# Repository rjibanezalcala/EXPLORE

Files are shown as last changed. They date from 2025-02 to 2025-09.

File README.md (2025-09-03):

---

---

<h1 id="welcome-to-explore">Welcome to EXPLORE!</h1>
<p>EXPLORE stands for microElectrode eXperimental kit with Probe LOcation Rationalization in Electrophysiology. EXPLORE is an open-source collection of 3D-printed devices and protocols which aim to provide neuroscientists tools, methods, and guidelines to carry out electrophysiological experiments in rodents.</p>
<p>Here we provide 3D-printable files for our custom-made, modular, adjustable chronic implant designed to house one or two microelectrode array probes (such as the <a href="https://www.neuropixels.org">Neuropixels probes</a> or <a href="https://plexon.com/products/neural-electrodes-probes-and-arrays/">Plexon probes</a>). You will also find our custom “implant accessories”, including our implant stereotaxic holder, assembly kit, and testing kit. Last, but not least, we have designed KEPLER, a precision screwdriver which aims to assist in making micrometer-adjustments to the vertical position of the probe(s) as they are slowly introduced into the brain tissue within the implant.</p>
<p>Everything in this repository can be printed completely in-house with a consumer-grade SLA 3D printer. FDM printing is not recommended as the resulting print may not be durable or smooth enough to function correctly. We have printed and tested our implant using a <a href="https://www.formlabs.com">Formlabs</a> printer and Tough 2000 resin; Preform project files are provided herein. Other printers and/or similarly tough resins should theoretically work just as well, but we have not tested this.</p>
<p align="center">
<b><a href="https://doi.org/10.1016/j.crmeth.2025.101146">Find us on Cell Reports Methods!</a></b>
<br>

</p>
<h2 id="cami-our-chronic-adjustable-and-modular-implant">CAMI: our Chronic, Adjustable, and Modular Implant</h2>
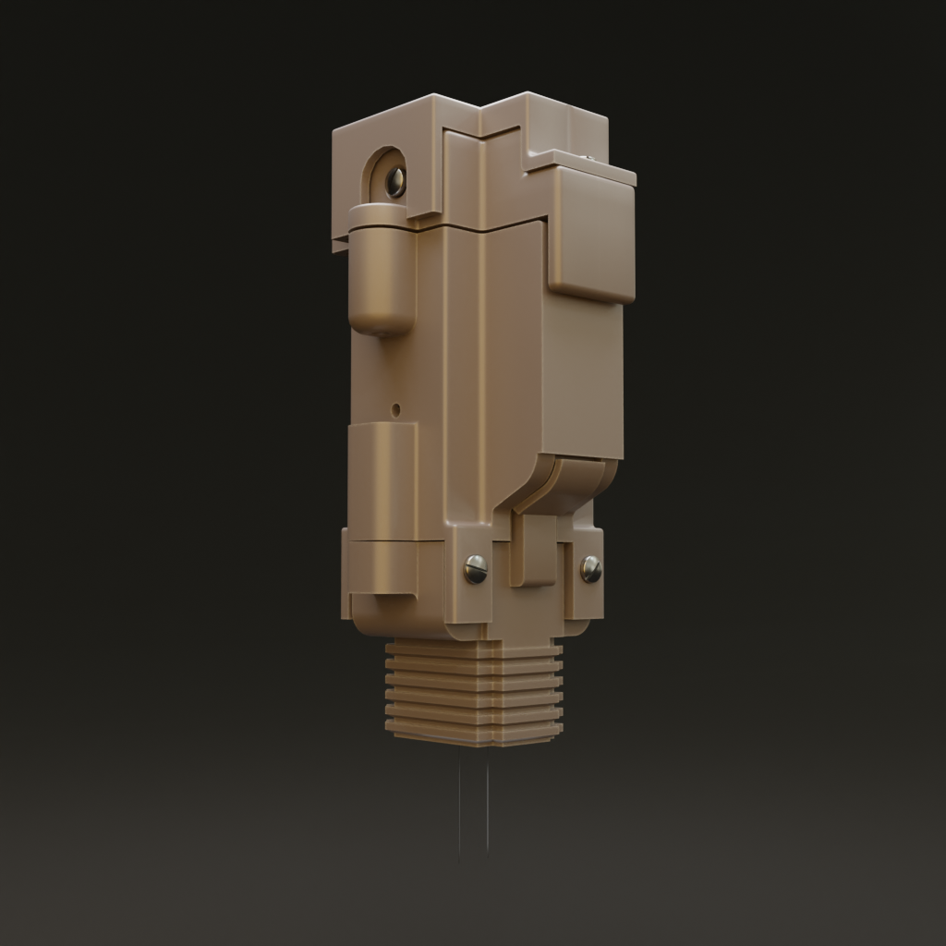
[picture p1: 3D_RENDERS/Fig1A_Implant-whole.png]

<p><a href="https://github.com/rjibanezalcala/EXPLORE/tree/9734e33baba4d4b4137d461dfe143eeaee72ebce/IMPLANTS">Our chronic implant</a> consists of five main parts: the skull interface, implant body, shuttle, headstage interface, and cap. Each piece is functionally (mostly) independent from the next and provides a solution to a specific problem; because of this, our implant is modular. Modularity is the biggest strength of our implant as it facilitates quick, pin-pointed modifications to adapt the implant to different needs. The implant uses a screw mechanism to push the probe(s) vertically within the implant.</p>
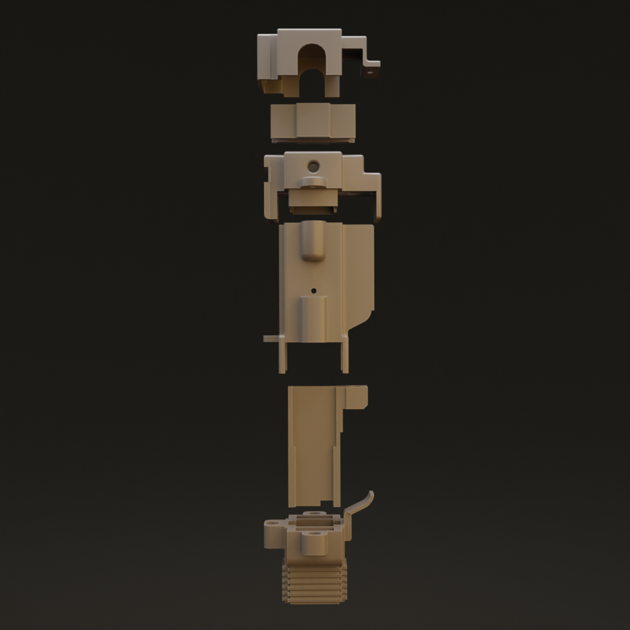
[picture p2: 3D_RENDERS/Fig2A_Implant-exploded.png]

<p><a href="https://github.com/rjibanezalcala/EXPLORE/tree/9734e33baba4d4b4137d461dfe143eeaee72ebce/IMPLANTS/Base_implant">Go to the base CAMI implant directory</a></p>
<p><strong>Skull interface.</strong> The bottom of this piece will come in direct contact with the animal’s skull. It measures 8.3 x 11.6 mm at the bottom and has one hole on each side for the probe shank to come out of the implant. Ridges are located around the bottom to better hold on to the dental cement that is applied to hold the implant in place. At the top, it has a small piece which covers the bottom of the implant body’s side rail to protect the inside from debris.</p>
<p><strong>Shuttle.</strong> The shuttle piece holds up to two electrode array probes on its probe beds. In its basic design, it is made to hold a Neuropixels (NP) 1.0 probe on each side, however the probe bed can be modified to hold probes of different form factors if desired (<a href="https://github.com/rjibanezalcala/EXPLORE/tree/504db79cb99880db6802545523e33a635f92d3f8/IMPLANTS/2.0_version">see 2.0 mod</a>). The basic design provided herein provides a 1.5 mm probe separation from the midline, or a 3 mm separation from probe to probe.</p>
<p><strong>Implant body.</strong> This is the largest part of the implant. It sits between the skull interface and headstage interface and houses the shuttle piece which carries the probe(s). Inside it, a mid-line and side rail guides the shuttle piece along the vertical axis, preventing it from moving on the other two axes. It is also reinforced with a molded grid structure on the inside to better protect the fragile probes from impact.</p>
<p><strong>Headstage interface.</strong> This piece allows access to the NP probes’ Flat Printed Circuit (FPC) connectors while also holding them in place to mate them with a headstage’s Zero Insertion Force (ZIF) connector. It features a “biting” mechanism to do this, where two flat plastic pieces are inserted and tightened against the middle of the headstage interface to push the FPCs into a recessed area which prevents them from being pushed down during headstage connection. The spacing between FPCs was originally intended for an Open Ephys ONIX Neuropixels 1.0 headstage, however it can be modified for other headstages.</p>
<p><strong>Cap.</strong> This piece simply covers the probes’ FPCs to protect them from debris. It is held down by a small internal latch and a small screw. We provide both high and low-profile versions, with the low-profile version being the shortest of the two.</p>
<h3 id="cami-modifications-mods">CAMI modifications (mods)</h3>
<p>We have designed CAMI to be modular because it gives the end user the most power to make modifications to the device or use parts of the device as needed. Because the implant is modular, adapting it to different needs can be as simple as modifying only the pieces that need to be modified. We have provided modified implant pieces for different purposes to demonstrate this. To demonstrate how designing the implant for a smaller probe (in this case the Neuropixels 2.0), we have provided the <a href="https://github.com/rjibanezalcala/EXPLORE/tree/9734e33baba4d4b4137d461dfe143eeaee72ebce/IMPLANTS/2.0_version">2.0 mod</a>. We have also adapted the implant to fit <a href="https://github.com/rjibanezalcala/EXPLORE/tree/9734e33baba4d4b4137d461dfe143eeaee72ebce/IMPLANTS/E-stim_version">electrical stimulation electrodes</a> and <a href="https://github.com/rjibanezalcala/EXPLORE/tree/9734e33baba4d4b4137d461dfe143eeaee72ebce/IMPLANTS/Opto_version">optogenetic optical fibres</a> as well. <strong>It is important to note that the modified implant versions in this repository have not been tested as this was outside of the scope of this project</strong>, they simply serve as a demonstration of how modularity allows pinpointed modifications without having to modify other parts of the implant.</p>
<p><em>IMPORTANT: All implant files were exported from Blender scaled up by a factor of 10.</em></p>
<h2 id="kepler">KEPLER</h2>
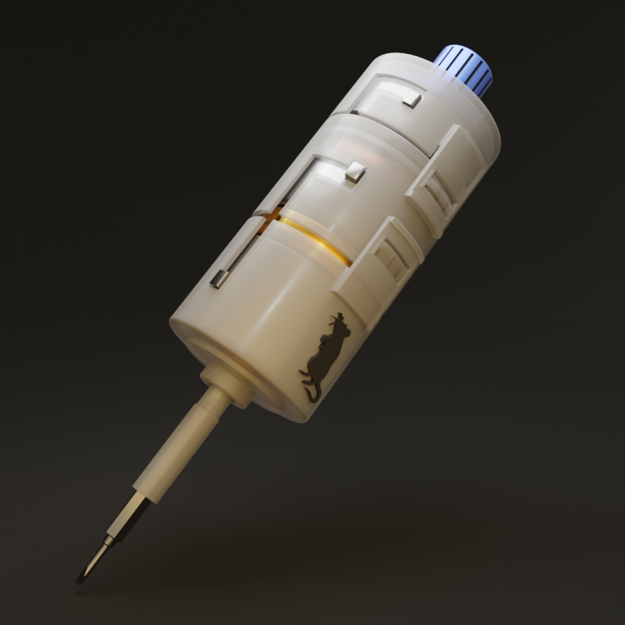
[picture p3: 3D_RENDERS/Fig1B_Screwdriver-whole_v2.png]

<p>KEPLER is a screwdriver with a mechanical gear system encased inside it. It is named after Johannes Kepler, a German astronomer and mathematician best known for his <em>Laws of Planetary Motion</em>. KEPLER’s internal mechanism consists of a series of concentric, cascading <em>planetary gear systems</em> (hence the planetary motion) which slow down the user’s input turns 25 times and transfers them to its output. When coupled with a screw mechanism, the driving screw’s turns are subdivided, effectively allowing the user to make turns which will translate into micrometer-level movements.</p>
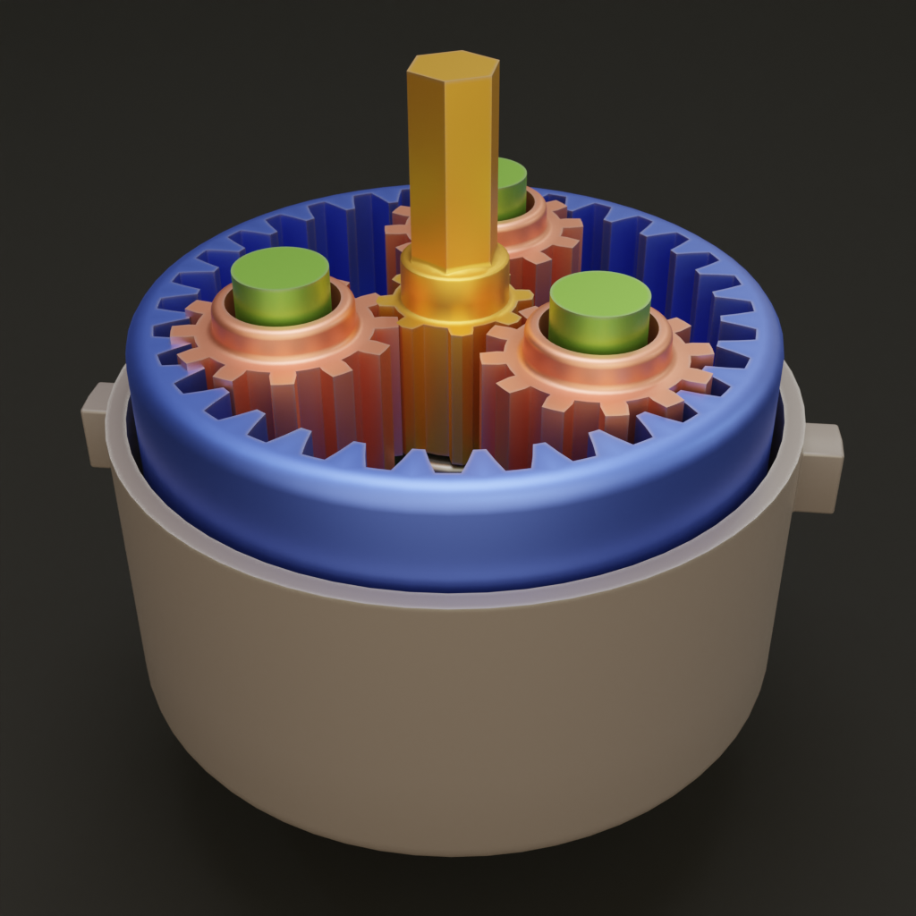
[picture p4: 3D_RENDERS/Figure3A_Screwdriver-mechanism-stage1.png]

<p>In a screw mechanism, an object is “pushed” or “pulled” along the shaft of the driving screw. Each turn moves the object a distance equal to the screw’s <em>pitch</em>, or the space between each thread. Subdividing the screw’s turns will subdivide that distance proportionally, and if the pitch is small enough, each subdivision will result in a distance in the order of 10’s of micrometers. For example, if the pitch of the screw is 0.3 mm, half a turn will result in 0.15 mm. With one <em>full</em> turn at its input, KEPLER can reduce this down to 0.3/25 = 0.012 mm, or 12 um. This can be reduced further if only a half or quarter turn is made with KEPLER.</p>
<p><em>IMPORTANT: The files for KEPLER were exported from Blender scaled up by a factor of 1.5.</em></p>
<p><a href="https://github.com/rjibanezalcala/EXPLORE/tree/9734e33baba4d4b4137d461dfe143eeaee72ebce/KEPLER">Go to KEPLER directory</a></p>
<h3 id="why-so-much-precision">Why so much precision?</h3>
<p>Slow and controlled foreign body insertions into the brain tissue can not only reduce inflammation but also protect the fragile probe shanks from breaking by reducing the force that pushes them down. Precise adjustments are also useful when targeting and recording from specific areas of the rodent brain, which tend to be very small.</p>
<h2 id="implant-accessories">Implant accessories</h2>
<p>Implant accessories aim to facilitate implant assembly, testing, and surgery.</p>
<p><em>IMPORTANT: All implant accessory files were exported from Blender scaled up by a factor of 10.</em></p>
<h3 id="assembly-kit">Assembly kit</h3>
<p>Assembling the implant is a delicate process which requires a lot of steady and slow movements to avoid breaking the fragile probes. A stereotaxic device can offer the stability needed to safely assemble the implant; thus, we designed our assembly kit around it. The kit includes a block to hold the implant components and probes as the whole device is assembled and a stereotaxic holder made specifically for loading the probe(s) into the implant. The assembly process is best done with the aid of a surgical microscope (if available) to keep an eye on the shanks to avoid breaking them.</p>
<p><strong>Implant holding block.</strong> During assembly, the probe shanks are exposed to damage from regular handling. To prevent accidents, the holding block is tall enough to encase the full length of probe shanks, and sturdy enough to stabilize the different implant pieces during assembly. We have also included an anchor tail on the holding block to keep it in place while loading the probes.</p>
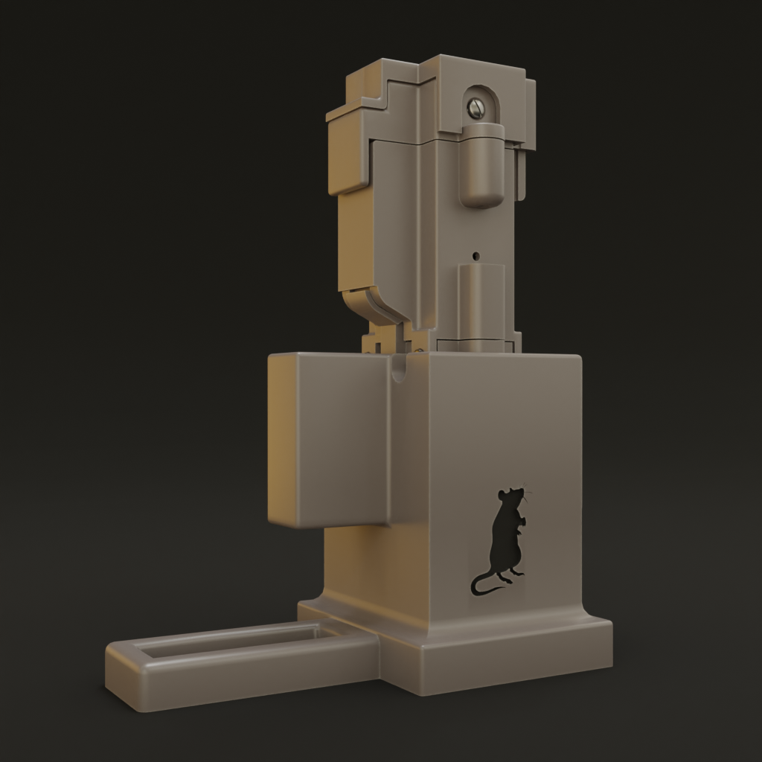
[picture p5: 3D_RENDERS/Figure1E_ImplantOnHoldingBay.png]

<p><strong>Shuttle stereotaxic holder.</strong> To leverage the movement stability of a stereotaxic device for loading probes onto our implant, we designed a stereotaxic holder made to carry the shuttle piece and probes so that they can be manoevered around with precision.</p>
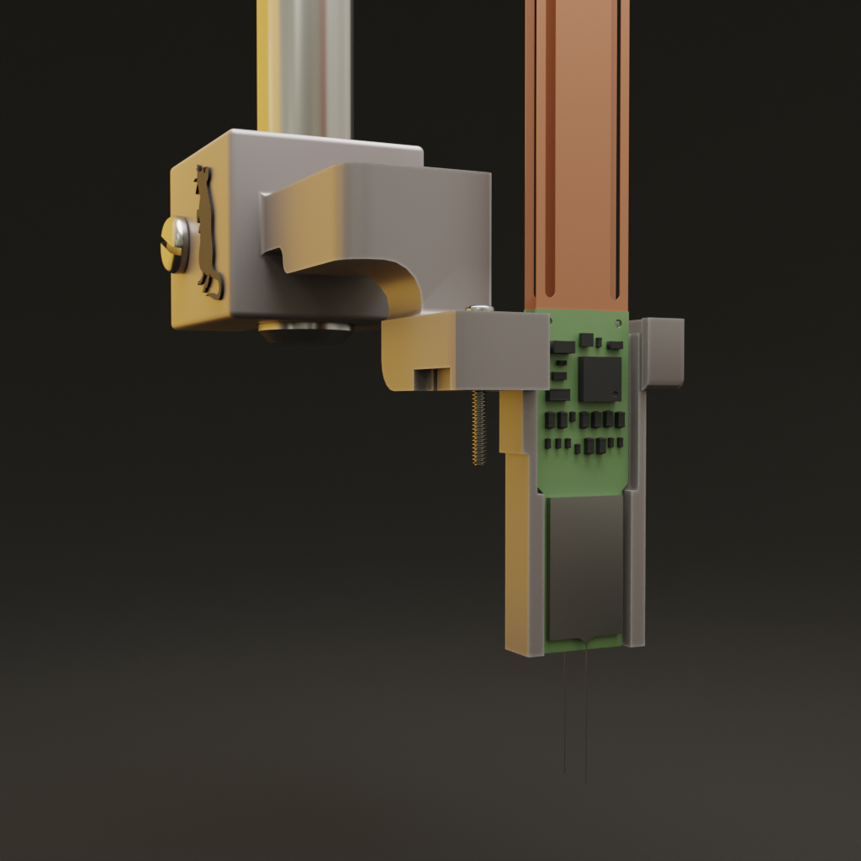
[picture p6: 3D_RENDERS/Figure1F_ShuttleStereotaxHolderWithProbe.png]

<p><a href="https://github.com/rjibanezalcala/EXPLORE/tree/9734e33baba4d4b4137d461dfe143eeaee72ebce/ASSEMBLY_KIT">Go to assembly kit directory</a></p>
<h3 id="surgery-kit">Surgery kit</h3>
<p>As a part of the surgery kit, we provide a stereotaxic holder made to carry the fully assembled implant during surgery. The holder is made to firmly grip onto the implant during surgery, but also to gently release it when done. It does so through tightening or loosening a screw and nut on the holder.</p>
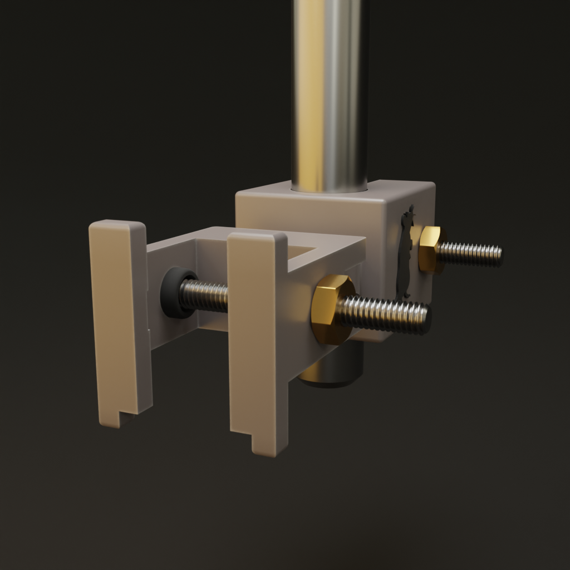
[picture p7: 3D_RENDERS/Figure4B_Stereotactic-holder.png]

<p>We have also provided the <a href="https://github.com/rjibanezalcala/EXPLORE/blob/222c10cda8db09f74cfceb7bc71986f99791b9b0/SURGERY_KIT/EXPLORE_surgical_calculator_blank.xlsx">Excel sheet</a> we used to keep track of probe depth after surgery and each micro-adjustment made with KEPLER. On the first sheet, you’ll find a calculator that translates direct drive screw turns into a distance based on the screw’s pitch. It also calculates the same distance as a function of screw turns made with KEPLER. The Probe depth log sheet helps figure out how much to draw the probes out of the implant to reach a certain location (see our published paper for details, under Methods ‘Calculating probe location on the vertical axis’). In short, the total distance to draw the probes out is a function of how thick the skull interface bottom wall is, the target depth, and the skull thickness. The calculator can help figure out how much to turn the drive screw to draw the probe out to this distance.</p>
<p><a href="https://github.com/rjibanezalcala/EXPLORE/tree/9734e33baba4d4b4137d461dfe143eeaee72ebce/SURGERY_KIT">Go to surgery kit directory</a></p>
<h3 id="test-kit">Test kit</h3>
<p>It is generally good practice to carry out noise and gain tests on an electrode <em>before</em> implanting it on an animal. This is typically done by submerging the recording electrode(s) in saline solution and reading the signal that is picked up from within the solution. For a noise test, simply recording from within the saline is enough to infer the noise properties of the recording device, however for gain tests a test signal is transmitted through the saline and picked up by the electrode. The recorded signal’s nominal amplitude is compared to the test signal’s amplitude to make inferences about the device.</p>
<p>Although the hardware setup to conduct such tests is fairly simple, a lab may not always possess the materials necessary to construct it. For this reason, we provide a 3D printable saline bath testing environment. The setup simply includes a basin for the saline, spaces to glue conductive electrodes to run a rest signal, and a detachable mini-holding block for the implant.</p>
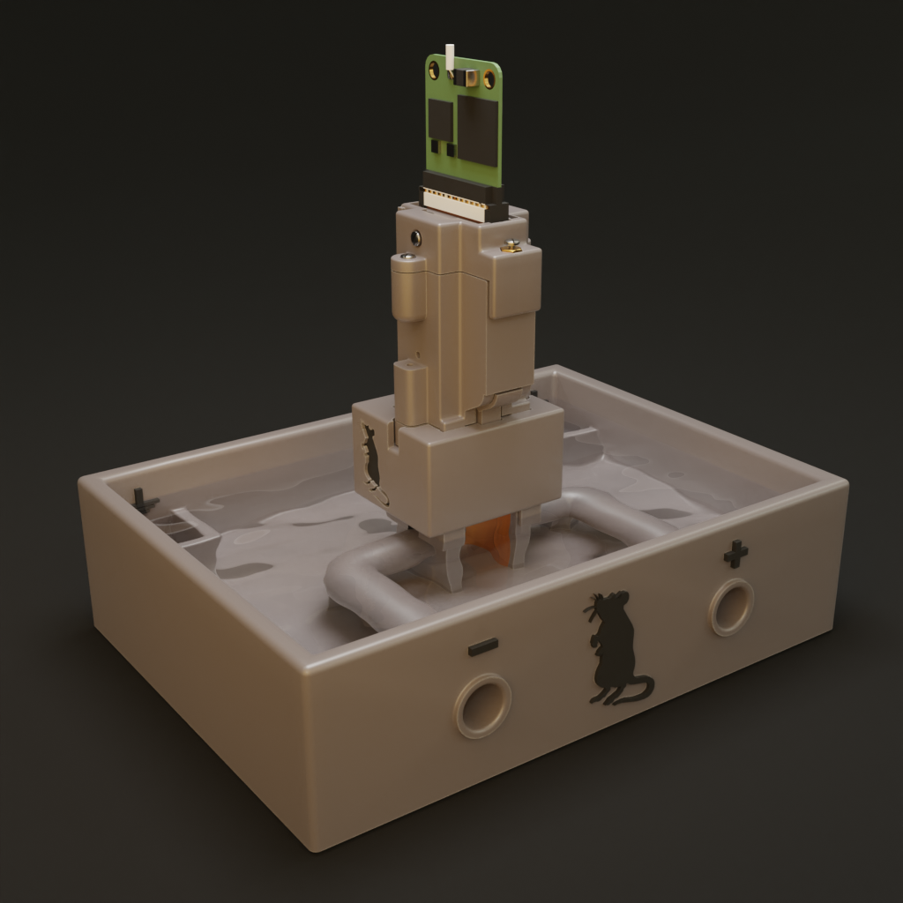
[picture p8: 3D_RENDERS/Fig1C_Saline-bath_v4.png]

<p>The saline bath can be used with or without the mini-holding block; if used without, one may opt for using one of our stereotaxic holders.</p>
<p>Assembling the saline bath is as simple as cutting two copper plates (10 mm x 19.5 mm), running a wire through each tube from the front, then soldering the wires to the plates. The length of the wire can be 20 - 30 cm or more, if desired. We crimped one banana connector to each wire end to ensure compatibility with the <a href="https://www.ampi.co.il/iso-flex">A.M.P.I. Iso-flex Electrical stimulus isolator</a>. We recommend affixing the copper plates with silicone sealant and letting it dry for at least 24 hours to ensure a watertight seal.</p>
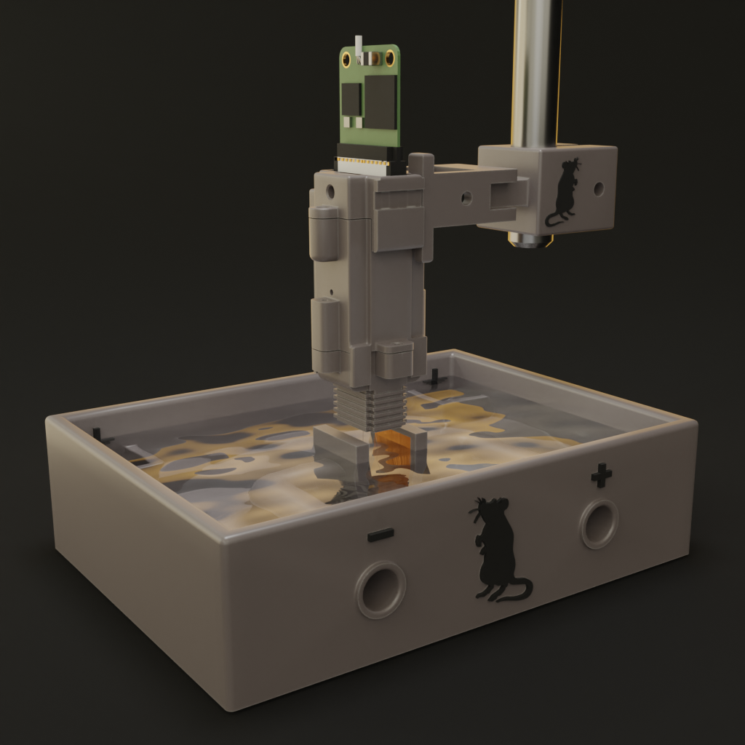
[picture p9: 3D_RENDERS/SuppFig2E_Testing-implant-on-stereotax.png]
<p align="center">
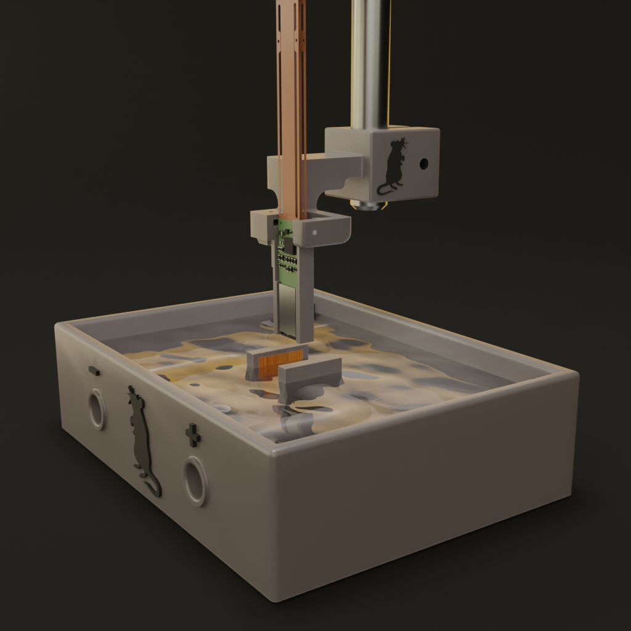
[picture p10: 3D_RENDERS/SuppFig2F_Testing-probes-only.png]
</p>
<p><a href="https://github.com/rjibanezalcala/EXPLORE/tree/9734e33baba4d4b4137d461dfe143eeaee72ebce/TEST_KIT">Go to test kit directory</a></p>
<hr>
<p> All 3D files provided within this repository alongside with the 3D rendered images were made from scratch in Blender 3.4.0. The original .blend files can be found <a href="https://github.com/rjibanezalcala/EXPLORE/tree/9734e33baba4d4b4137d461dfe143eeaee72ebce/BLENDER">here</a>.</p>
<p>Additional 3D assets pictured in <a href="https://github.com/rjibanezalcala/EXPLORE/tree/6d3b0f511474fb4baaf2f610220c143b38338c0d/3D_RENDERS">rendered images</a> such as fastenings (screws, nuts, and threaded inserts) and Neuropixels probes (1.0 and 2.0) were downloaded free of charge; sources are listed below.</p>
<ul>
<li><a href="https://hhmi.flintbox.com/technologies/018e9ed4-bc90-498e-a442-1853e33a690a">3D modelled Neuropixels 1.0 probe provided by Svoboda and Harris Labs</a></li>
<li><a href="https://hhmi.flintbox.com/technologies/efa0484d-5343-4b62-8142-d09de5341c43">3D modelled Neuropixels 2.0 probe provided by Svoboda and Harris Labs</a></li>
<li><a href="https://mcmaster.com">3D modelled fastenings provided by McMasterCarr</a></li>
</ul>
<p>All headstage 3D models pictured were hand-modelled from scratch and represent the <a href="https://github.com/open-ephys/onix-headstage-neuropix1">Open Ephys ONIX Neuropixels 1.0 headstage</a>, and the <a href="https://www.neuropixels.org/probes-np1-0">Neuropixels 1.0 headstage</a> with approximate dimensions. Their only purpose was to aid in the design, 3D modelling, and testing of the implants; <a href="https://github.com/rjibanezalcala/EXPLORE/tree/8049b335174be6d445f9110f4b5e6c4adbbae4cc/DUMMY_HEADSTAGES">they can be found here</a>.</p>
<p><a href="https://skfb.ly/6BBGs">Coin model and textures provided by MilaHigher</a> under Creative Commons Attribution License.  Model was upscaled to 24.26 mm diameter and 1.75 mm thickness to match the dimensions of a USD quarter.</p>

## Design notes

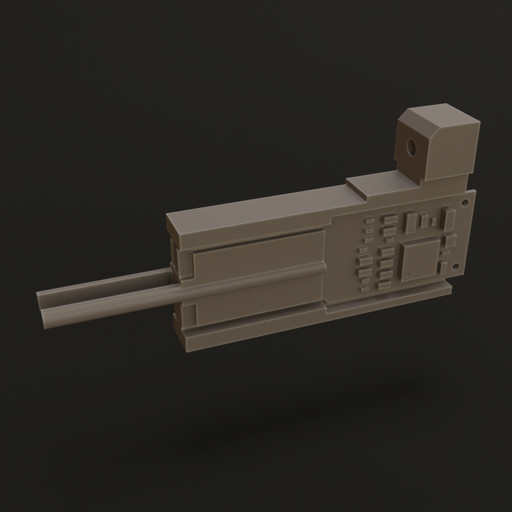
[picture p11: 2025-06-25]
3D_RENDERS/resize_practice_shuttle.png

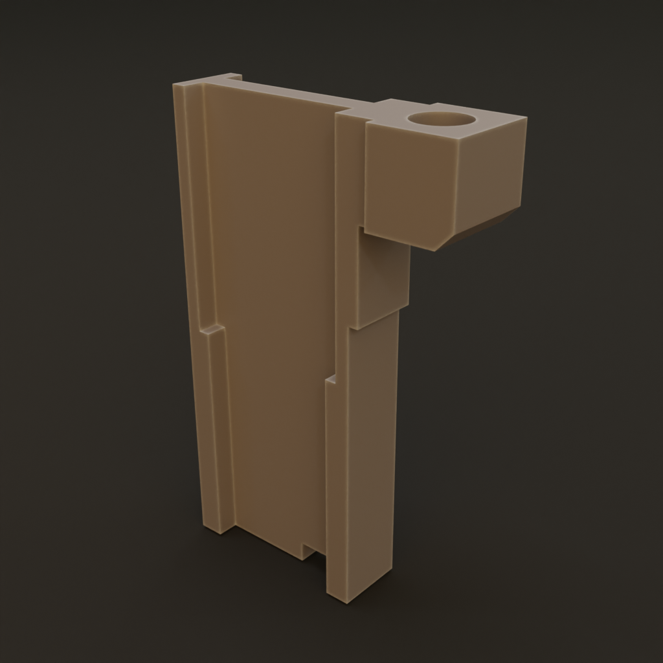
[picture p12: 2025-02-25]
3D_RENDERS/Fig2C_Shuttle.png

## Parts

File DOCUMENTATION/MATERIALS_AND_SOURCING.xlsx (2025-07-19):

 | Part | Quantity | Supplier | Supplier ID
Fastenings | M1 x 4 screw | 2 pack (pk) | McMaster Carr | 91430A151 (https://www.mcmaster.com/91430A151)
 | M1.4 x 12 screw (0.3 mm pitch) | 1 pk. |  | 91800A711 (https://www.mcmaster.com/91800A711)
 | M1.4 x 4 screw | 2 pk. |  | 91430A156 (https://www.mcmaster.com/91430A156)
 | M6 x 15 screw (optional, if using aluminium breadboard) | 1 |  | 90128A335 (https://www.mcmaster.com/90128A335)
 | M1 threaded insert | 1 pk. |  | 92120A110 (https://www.mcmaster.com/92120A110)
 | M1.4 threaded insert | 1 pk. |  | 92120A140 (https://www.mcmaster.com/92120A140)
 | M1 nut | 3 pk. |  | 90591A311 (https://www.mcmaster.com/90591A311)
 | M2.6 x 25 screw | 1 pk. |  | 90353A120 (https://www.mcmaster.com/90353A120)
 | M2.6 nut | 1 pk. |  | 90592A008 (https://www.mcmaster.com/90592A008)
Hardware | Drill bit 1.0 mm | 1 | McMaster Carr | 2958A25 (https://www.mcmaster.com/2958A25)
 | Drill bit 1.4 mm | 1 |  | 2958A34 (https://www.mcmaster.com/2958A34)
 | Drill bit 7/64 in | 1 |  | 2901A507 (https://www.mcmaster.com/2901A507)
 | Slotted screwdriver bit 2mm, with 4mm hex shank | 1 |  | 5750A375 (https://www.mcmaster.com/5750A375)
 | Slotted screwdriver bit 1.5 mm, with 4mm hex shank | 2 |  | 5750A373 (https://www.mcmaster.com/5750A373)
 | Drill | 1 | Grainger
 | Soldering iron | 1 |  | 799RP8 (https://www.grainger.com/product/WELLER-Solering-Station-1-Channel-799RP8)
 | Solder | ? |  | 19YP69 (https://www.grainger.com/product/AMERICAN-BEAUTY-Solder-Wire-1-32-in-x-11-g-19YP69)
 | Lubricant oil | 1 |  | 41MW02 (https://www.grainger.com/product/3-IN-ONE-Machine-Oil-Multipurpose-Oil-41MW02)
 | Silicone glue | 1 |  | 22N770 (https://www.grainger.com/product/GE-Silicone-Sealant-Premium-Silicone-22N770)
 | Sandpaper
 | UV resin
 | Copper or copper alloy sheet
 | Plastic tip tweezers | 1 | DigiKey | 2014-2ACFR.SA.1.ITU-ND (https://www.digikey.com/en/products/detail/ideal-tek-s-a/2ACFR-SA-1-ITU/9664517)
 | Aluminium breadboard (optional) | 1 | Thorlabs | MB3060/M (https://www.thorlabs.com/thorproduct.cfm?partnumber=MB3060/M)
 | Screwdriver | 1 | StarTech | CTKRPR (kit including slotted screwdriver bit) (https://www.startech.com/en-us/computer-parts/ctkrpr)
Electronics | Pin connector male (x2 if 2 probes) | 30 | DigiKey | 350-10-101-00-006000 (https://www.digikey.com/en/products/detail/mill-max-manufacturing-corp/350-10-101-00-006000/4456122)
 | Socket connector female (x2 if 2 probes) | 30 |  | 2-5331272-3 (https://www.digikey.com/en/products/detail/te-connectivity-amp-connectors/2-5331272-3/813479)
 | Silver or Stainless Steel PFA coated wire | 1 | A-M Systems | 786500 (https://www.a-msystems.com/p-796-pfa-coated-silver-wire.aspx)
 |  |  |  | 791600 (https://www.a-msystems.com/p-809-pfa-coated-stainless-steel-wire.aspx)
Implant printable components | Shuttle case | 1 | This paper | https://github.com/rjibanezalcala/EXPLORE/tree/main/IMPLANTS
 | Skull interface | 1
 | Probe shuttle | 1
 | Headstage interface | 1
 | Ribbon pincher | 2
 | Headstage interface cap | 1
 | Implant stereotactic holder | 1
 | Implant building aides | 1
 | Skull interface holding bay | 1
 | Shuttle elevator | 1
“Kepler” screwdriver printable components | Bottom casing | 1 | This paper | https://github.com/rjibanezalcala/EXPLORE/tree/main/KEPLER
 | Bottom casing shell | 1
 | Knob (small or large) | 1
 | Bit adapter | 1
 | Middle indicator | 1
 | Top casing | 1
 | Top casing shell | 1
 | Carrier | 2
 | Carrier spacer | 2
 | Planet gear | 6
 | Planet gear spacer | 6
 | Sun gear shaft | 1
 | Sun gear socket | 1
 | Sun spacer | 2
 | Ring gear | 2
 | Counter ring gear (optional) | 1
 | Counter carrier (optional) | 1
 | Counter carrier spacer (opt.) | 1
 | Counter planet gear (opt.) | 3
 | Counter planet gear spacer (opt.) | 3
 | Counter sun gear (opt.) | 1
 | Counter sun gear spacer (opt.) | 1
 | Counter knob (opt.) | 1
 | Counter adapter sun gear (opt.) | 1
 | Replaces one regular sun gear
 | Counter face (opt.) | 1
 | Counter shell (opt.) | 1
 | Top casing shell for counter module (opt.) | 1
 | Replaces regular top shell
Other 3D printables | Stereotactic implant holder | 1 | This paper | https://github.com/rjibanezalcala/EXPLORE
 | Stereotactic shuttle holder | 1
 | Implant “holding block” | 1
 | Saline bath (optional) | 1
3D printer and accessories | Tough 2000 photopolymer resin |  | Formlabs | RS-CFG-TO20-01 (https://formlabs.com/store/materials/tough-2000-resin/)
 | Clear V4 photopolymer resin |  |  | RS-CFG-GPCL-04 (https://formlabs.com/store/materials/clear-resin-v4/)
 | Resin tank V2.1 |  |  | RT-F3-02-01 (https://formlabs.com/store/accessories/form-3-resin-tank/)
 | Build platform |  |  | BP-F3-01 (https://formlabs.com/store/accessories/form-3-build-platform/)
 | Form3 SLA 3D printer, wash, and cure |  |  | PKG-F3-SVC-COMPLETE
Software | Blender |  | Blender | Blender 3.4.0 (https://download.blender.org/release/Blender3.4/)
 | Needed to make edits to implant
 | Preform |  | Formlabs | Preform (https://formlabs.com/software/preform/)
 | For printing using Formlabs 3D printers
 | Spike GLX |  | Github | Spike GLX (https://billkarsh.github.io/SpikeGLX/)
 | If using PXIe acquisition system
 | Open Ephys GUI |  | Open Ephys | Open Ephys GUI (https://open-ephys.org/gui)
 | If using PXIe acquisition system, alternative to SpikeGLX
 | Bonsai |  | Bonsai RX | Bonsai (https://bonsai-rx.org/)
 | If using ONIX acquisition system
Recording equipment | Neuropixels 1.0 probe |  | Neuropixels | PRB_1_4_0480_1 (https://www.neuropixels.org/probe1-0)
 | 1.0 headstage and cable |  |  | HS_1000, CBL_1000 (https://www.neuropixels.org/probes-np1-0)
 | If using PXIe acquisition system (see below)
 | PXIe card |  |  | PXIE_1000 (https://www.neuropixels.org/system1-0)
 | If using PXIe acquisition system (see below)
 | PXIe-1082 Chassis |  | National Instruments | https://www.ni.com/en-us/support/model.pxie-1082.html
 | ONIX PCIe Acquisition System |  | Open Ephys | OEPS-9006 (https://open-ephys.org/onix/oeps-9006)
Other hardware | A.M.P.I. Iso-flex Electrical stimulus isolator |  | A.M.P.I. | Iso-flex (https://www.ampi.co.il/iso-flex)
 |  |  | Microprobes | USA seller (https://microprobes.com/products/neuroscience-research-equipment/iso-flex)
 | A.M.P.I. Master-9 pulse stimulator |  | A.M.P.I. | Master-9 (https://www.ampi.co.il/master-9)
 |  |  | Microprobes | USA seller (https://microprobes.com/products/neuroscience-research-equipment/master-9)
Surgical supplies | Metabond Kit |  | Parkell | https://www.parkell.com/C-B-Metabond-Quick-Adhesive-Cement-System
A detailed list of materials used for implant assembly, as well as electronic equipment, software, and key surgical supplies. Most suppliers are located in the United States.

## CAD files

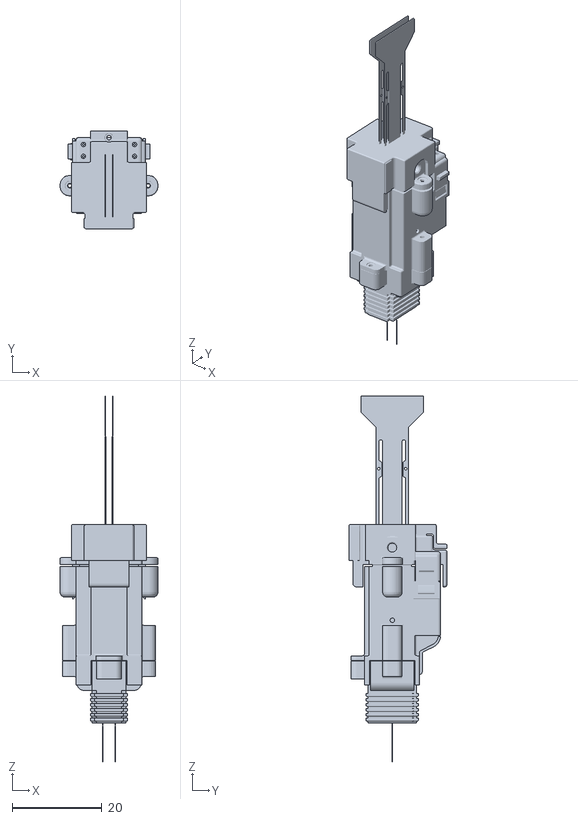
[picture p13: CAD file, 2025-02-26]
IMPLANTS/E-stim_version/Estim_implant_full.stl
21.9 x 21.9 x 81.5

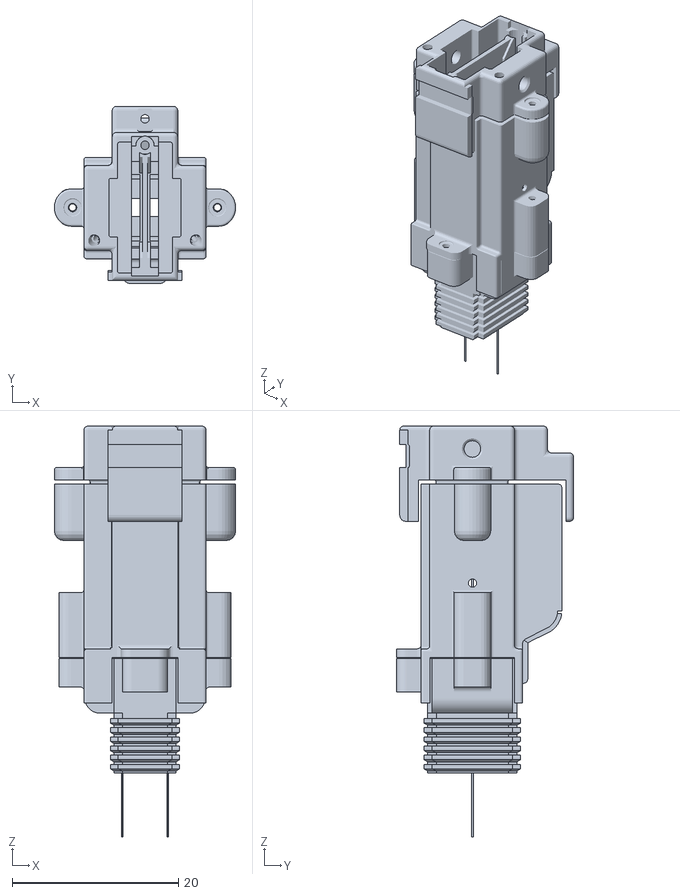
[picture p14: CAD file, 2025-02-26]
IMPLANTS/Opto_version/Opto_implant_full.stl
21.9 x 21.4 x 49.5

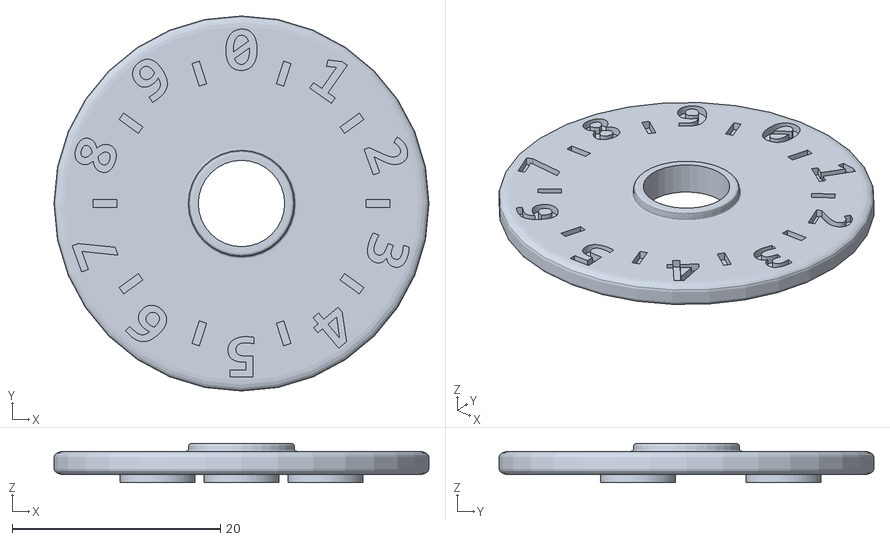
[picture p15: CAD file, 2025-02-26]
KEPLER/Rotary_counter/Counter_wholes_dial_v2.stl
36.0 x 36.0 x 3.75

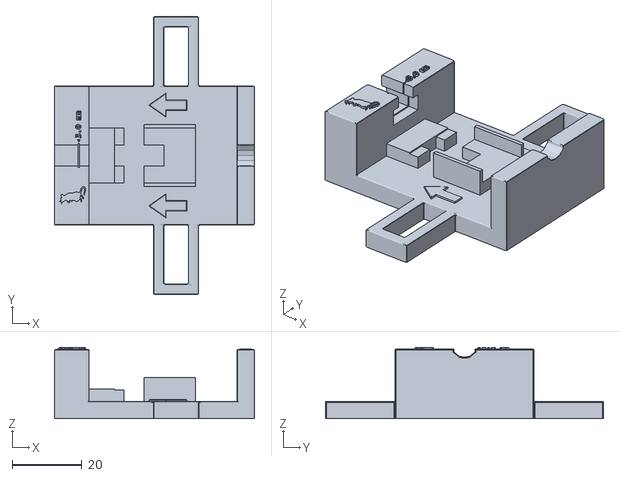
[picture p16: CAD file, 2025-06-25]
ASSEMBLY_KIT/calibration_block_v2.stl
57.6 x 80.0 x 20.6

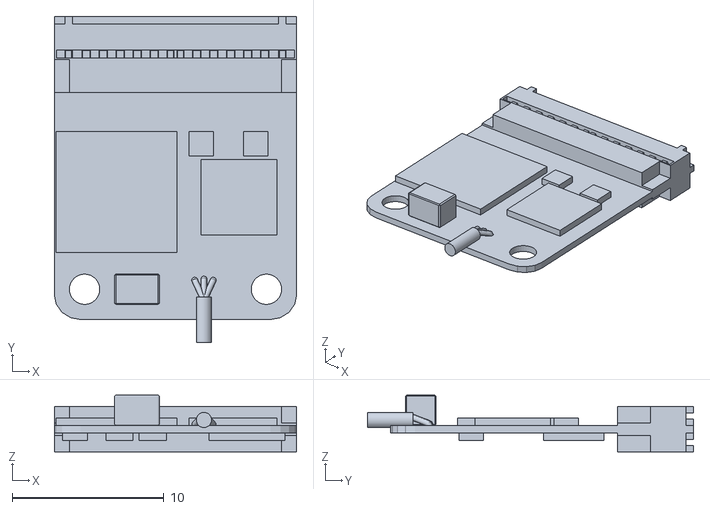
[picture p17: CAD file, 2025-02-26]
DUMMY_HEADSTAGES/Dummy_ONIX_NP1-0_headstage_v3.stl
16.0 x 21.5 x 3.75

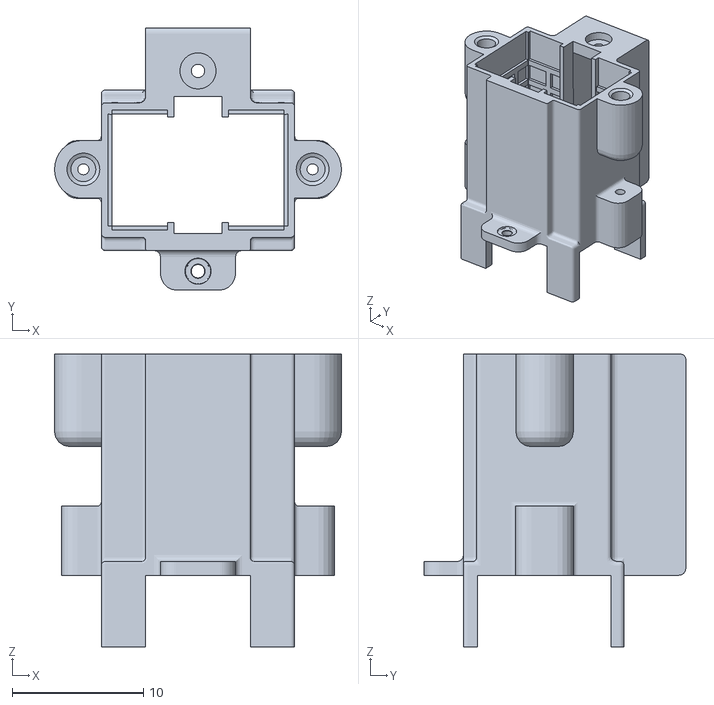
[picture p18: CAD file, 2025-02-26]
IMPLANTS/2.0_version/2-0_implant_body.stl
21.9 x 19.9 x 22.3

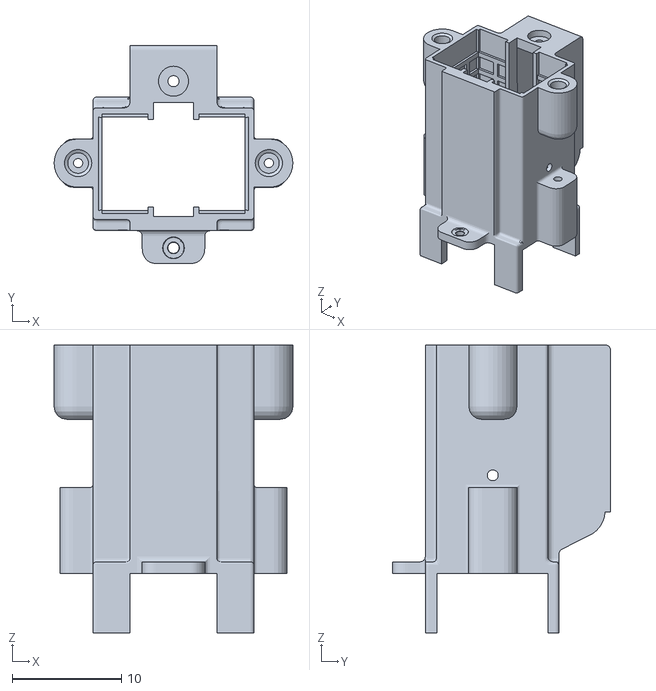
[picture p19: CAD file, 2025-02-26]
IMPLANTS/Base_implant/Implant_body_v5_ribbed.stl
21.9 x 19.9 x 26.4

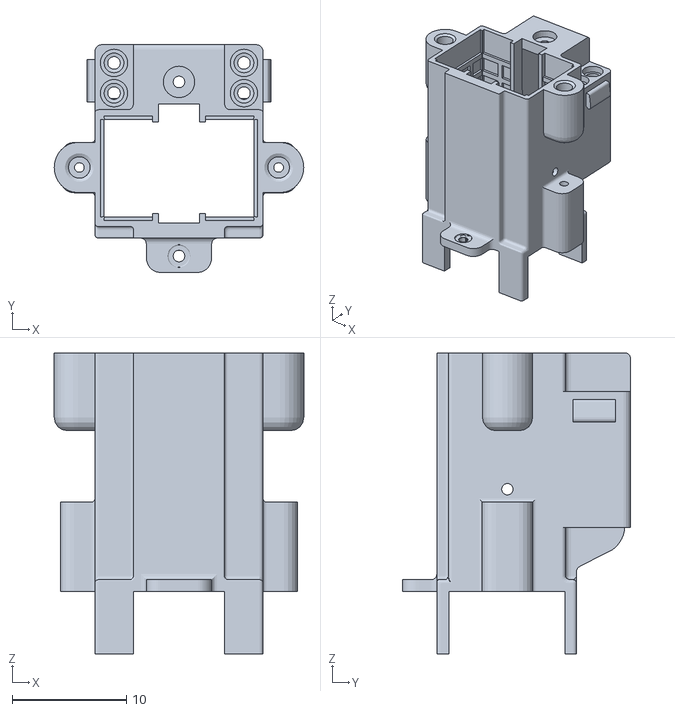
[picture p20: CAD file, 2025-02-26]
IMPLANTS/E-stim_version/Estim_implant_body.stl
21.9 x 19.9 x 26.4

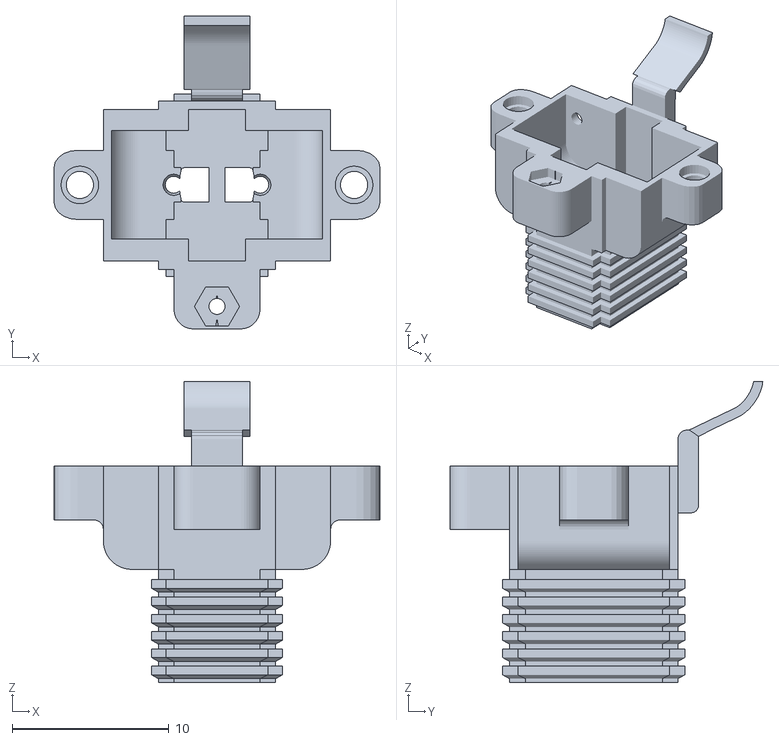
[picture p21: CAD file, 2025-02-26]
IMPLANTS/Opto_version/Opto_skull_interface.stl
20.8 x 19.9 x 19.2

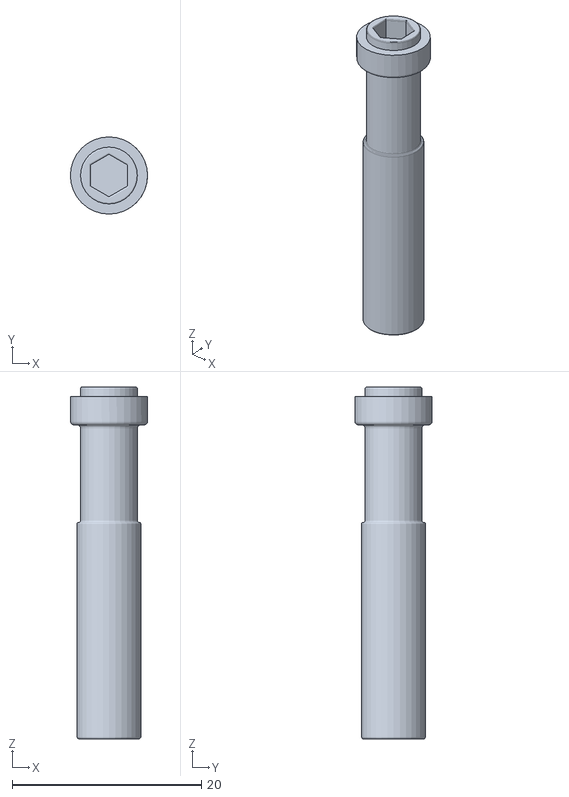
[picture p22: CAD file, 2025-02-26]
KEPLER/Casing/output_bit.stl
8.16 x 8.15 x 37.2

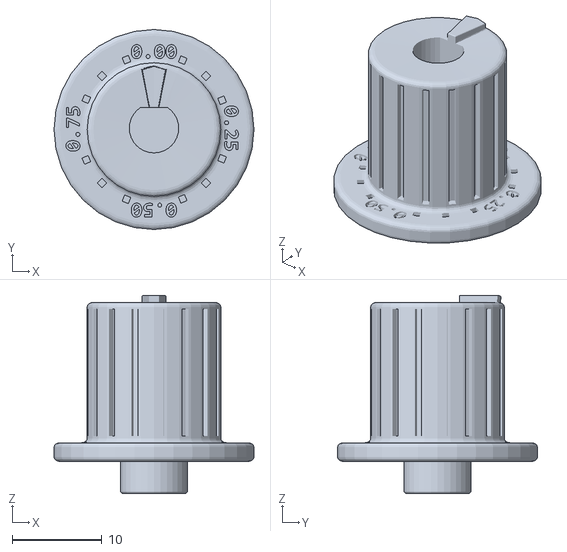
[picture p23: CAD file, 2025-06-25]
KEPLER/Counter_decimal_dial_round_socket.stl
22.3 x 22.3 x 22.1

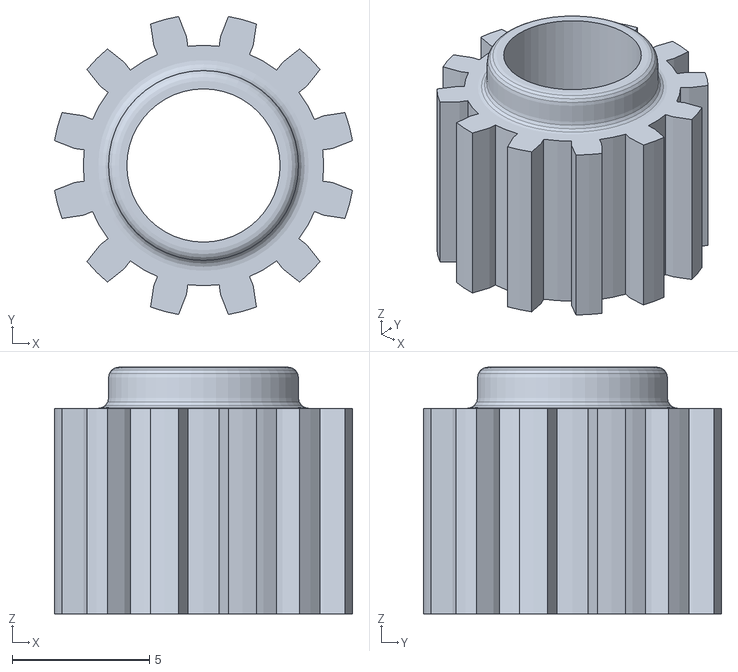
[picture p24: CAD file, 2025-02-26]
KEPLER/Planetary_gear_system/planet_gear_v2.stl
10.9 x 10.9 x 9.00

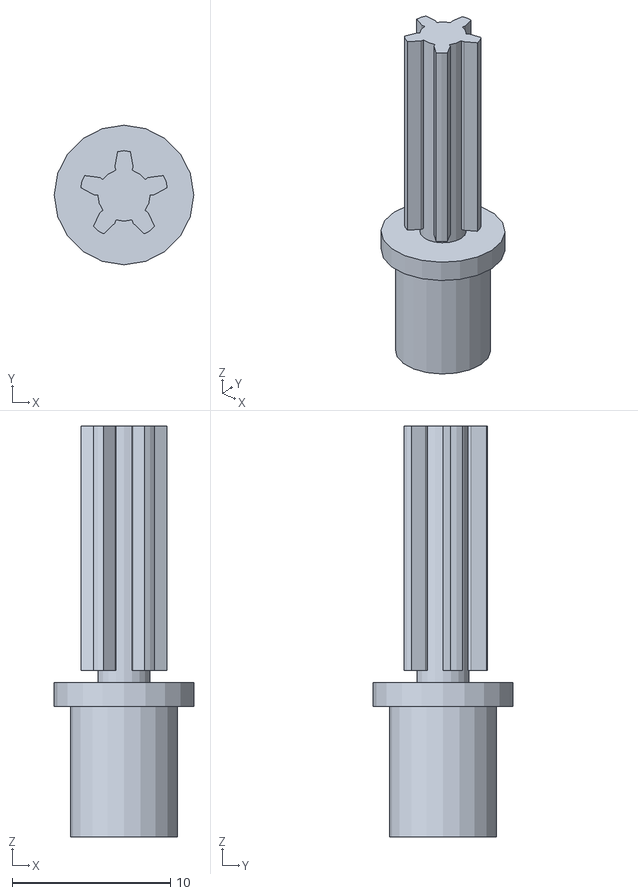
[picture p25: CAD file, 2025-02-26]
KEPLER/Rotary_counter/Counter_sun_gear_v2.stl
8.81 x 8.81 x 25.9

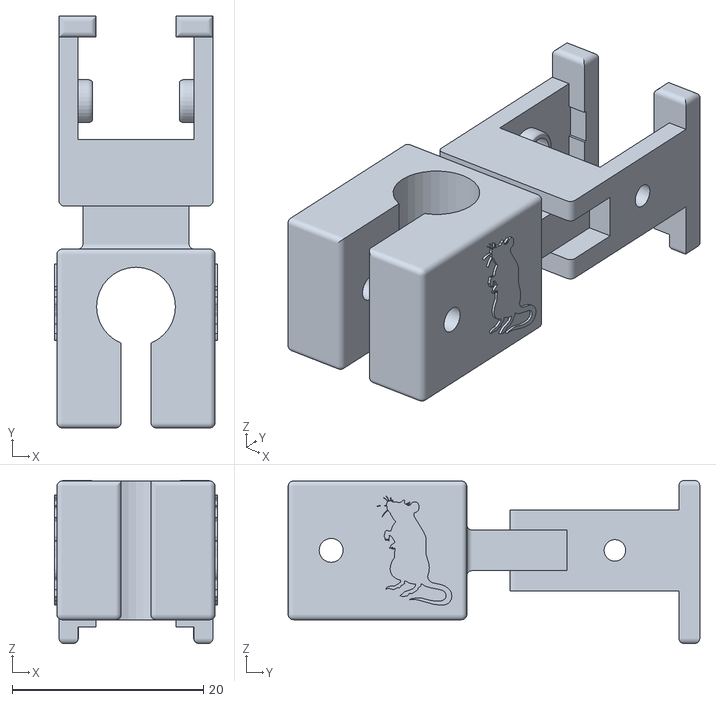
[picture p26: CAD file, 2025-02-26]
SURGERY_KIT/Implant_stereotaxic_holder_v2.stl
17.1 x 43.1 x 17.1

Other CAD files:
ASSEMBLY_KIT/Probe_shuttle_v3_TEST_DUMMY.stl
DUMMY_HEADSTAGES/Dummy_NP1-0_headstage.stl
IMPLANTS/2.0_version/2-0_shuttle.stl
IMPLANTS/Base_implant/Skull_interface_v4.stl
ASSEMBLY_KIT/Implant_holding_block_double-hex_v3.stl
ASSEMBLY_KIT/Shuttle_stereotaxic_holder_v2.stl
IMPLANTS/2.0_version/2-0_skull_interface.stl
IMPLANTS/Base_implant/Headstage_interface_cap_(low profile)_v4.stl
IMPLANTS/Base_implant/Headstage_interface_cap_v4.stl
IMPLANTS/Base_implant/Headstage_interface_v8.stl
IMPLANTS/Base_implant/Probe_shuttle_v3.stl
IMPLANTS/Base_implant/Ribbon_pincher_v2.stl
IMPLANTS/E-stim_version/Estim_header_socket.stl
IMPLANTS/E-stim_version/Estim_skull_interface.stl
IMPLANTS/Opto_version/Opto_fibres_in_cannulae.stl
IMPLANTS/Opto_version/Opto_headstage_interface.stl
KEPLER/Casing/bottom_casing.stl
KEPLER/Casing/bottom_casing_shell.stl
KEPLER/Casing/knob_large.stl
KEPLER/Casing/knob_small.stl
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

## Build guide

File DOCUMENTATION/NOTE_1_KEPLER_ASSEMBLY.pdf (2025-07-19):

# Supplemental Note 1: “Kepler screwdriver” assembly

Assembly of the Kepler screwdriver, or simply Kepler driver does not require extra steps to post-process the 3D printed pieces such as drilling or sanding. It also does not require any fastenings to put together. However, we do recommend lubricating the planetary gears before putting the device together completely. We provide instructions on this within this assembly guide. Because this device is 3D printed, one may expect small imperfections on the components brought up by the printing process to cause minor issues in the device’s functionality. This can be resolved with repeated use of the device until movement of the components becomes smoother over time.

### Printing the Kepler driver components

It is recommended that every component is printed using an SLA printer (photopolymer resin printer) at a high resolution (for example 0.005 mm layer height) to ensure that component dimensions are as close to the designed dimensions as possible. FDM printers may not be able to offer this resolution and, because of the nature of the printing technique, may introduce imperfections that might interfere with the device’s operation.

We were able to successfully print and assemble several Kepler drivers and replacement parts using a Formlabs Form 3 and Clear V4 resin (see supplemental note 4 ‘Materials and sourcing’ under section ‘3D printer and accessories’). A different resin which offers good resolution may be used instead if desired, however this was not tested by us. Keep in mind that Clear V4 resin is relatively brittle and may break if the device is dropped but will withstand regular day-to-day use under normal conditions. Finally, because Clear V4 resin has the tendency to deform during post-curing when prints are not very dense, we recommend not doing a post-cure; instead, simply washing the screwdriver components and letting them cure at room temperature over time (may take up to 7 days) will ensure that the shape of the components is preserved.

All Kepler driver components are available as STL files in our GitHub repository (https://github.com/rjibanezalcala/EXPLORE). Pre-made Preform (see supplemental note 4 ‘Materials and sourcing’ under section ‘Software’) projects are also provided in the same repository for downloading and printing directly. The components list is shown below (Table S1.1, Fig. S1.1), which indicates what components are needed and how many of them to print. Note that the addition of the counter module is optional, however we recommend adding it as it counts the number of turns made at the input which can reduce user error. If the counter module is added, make sure you make the replacements indicated in Table S1.1. This list can also be found in Supplemental Note 4.

“Kepler” screwdriver | Bottom casing | 1
| Bottom casing shell | 1

printable
components
Knob (small or large)* | 1
Bit adapter | 1
Middle indicator | 1
Top casing | 1
Top casing shell** | 1
Carrier | 2
Carrier spacer | 2
Planet gear | 6
Planet gear spacer | 6
Sun gear shaft*** | 1
Sun gear socket | 1
Sun spacer | 2
Ring gear | 2
Counter ring gear (optional) | 1
Counter carrier (optional) | 1
Counter carrier spacer (opt.) | 1
Counter planet gear (opt.) | 3
Counter planet gear spacer (opt.) | 3
Counter sun gear (opt.) | 1
Counter sun gear spacer (opt.) | 1
Counter knob (opt.)* Replaces regular knob | 1
Sun gear shaft adapter for counter (opt.)*** Replaces one regular sun gear | 1

Counter face (opt.) | 1
Counter shell (opt.) | 1
Top casing shell for counter module (opt.)** Replaces regular top shell | 1
Table S1.1 | Kepler driver components list. This table shows all the 3D printable components
necessary to assemble the Kepler driver. Counter components (marked as optional) are not required to use the Kepler driver; however, the counter module does provide some readability to the device and is recommended. Items marked with ‘*’ indicate that one may replace the other if the counter module is to be used. Thus, if the counter module is added, print the top casing shell for counter module instead of the regular top casing shell and the sun gear shaft adapter for counter instead of the regular sun gear shaft. All listed components can be found in our GitHub repository at https://github.com/rjibanezalcala/EXPLORE/tree/main/KEPLER.

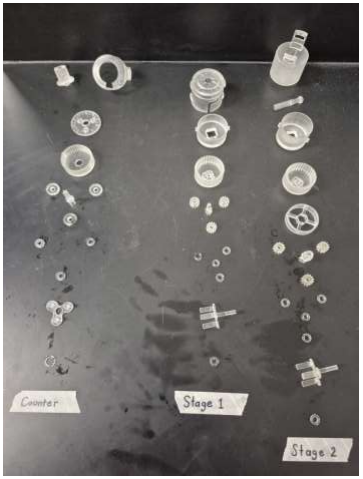
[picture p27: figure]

Figure S1.1 | Kepler components. The photograph shows all the Kepler driver components
classified by what subsystem of the device they belong to. The top components encompass the outer part of the device (shell) and the inner components are toward the bottom.

In summary:
a. Print Kepler driver components using an SLA printer with high-resolution compatible resin (this type of resin tends to be runnier) at a resolution of at least 0.005 mm layer height.
b. Do not post-cure the Kepler driver components, instead simply wash them and let them cure at room temperature for a few days. If post-curing is still desired, we recommend limiting the cure time.
c. All 3D printable components can be found alongside ready-to-print Preform projects at https://github.com/rjibanezalcala/EXPLORE/tree/main/KEPLER.
d. The components list and quantities are listed above in Table S1.1 or also under ‘”Kepler” screwdriver printable components’ in supplemental note 4.

### Assembling the planetary gear systems

Relevant components (screwdriver):
- Sun gear (shaft, and socket), 1 each.
- Replace sun gear (shaft) with sun gear shaft adapter for counter if printing a counter module.
- Sun gear spacer (regular), total of 2.
- Planet gears (regular), total of 6.
- Planet gear spacers (regular), total of 6.
- Ring gear (regular), total of 2.
- Gear carrier (regular), total of 2.
- Gear carrier spacer (regular), total of 2.
- Middle indicator, total of 1.

The main planetary gear systems
The instructions below assume only the components listed under “Relevant components (screwdriver)” (Fig. S1.2a).
1. Slide a sun gear spacer into the middle peg on each carrier. Then, slide one planet gear spacer into the three surrounding pegs (Fig. S1.2b).
2. Place a sun gear (shaft and socket) in the centre peg on each carrier (Fig. S1.2c), and one planet gear into each of the surrounding pegs (Fig. S1.2d). Wiggle the sun gear a bit if this gives you trouble.
3. Slide a carrier spacer on the bottom side of the carrier (on the longer shaft side (Fig. S1.2e), then slide the whole assembly into a ring gear (Fig. S1.2f). Repeat for the other carrier and ring gear.
4. Test the planetary gear systems by turning the sun gear in both directions. Lubricate the gears as needed.
5. Make sure to take note which one has the sun gear shaft, and which one has the sun gear socket and middle indicator, the former will be the stage 1 gear system, and the latter will be stage 2.
6. On the stage 2 gear system, slide the middle indicator piece onto the sun gear socket so that it sits on top of the whole gear system (Fig. S1.2g).
7. Set both gear systems aside for now (Fig. S1.2h).

A | B | C

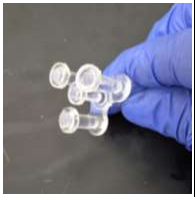
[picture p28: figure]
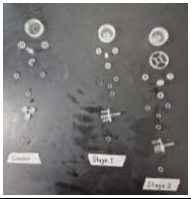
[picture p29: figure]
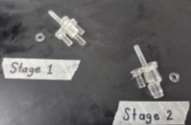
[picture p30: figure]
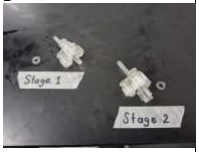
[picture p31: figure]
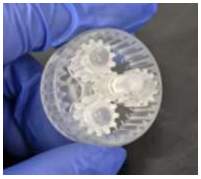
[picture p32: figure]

D | E | F

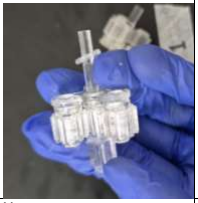
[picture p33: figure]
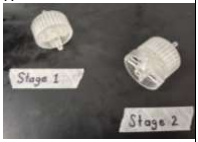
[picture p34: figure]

G | H

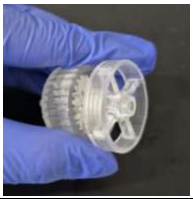
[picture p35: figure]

Figure S1.2 | Stage 1 and 2 gear systems assembly. a. Gear system components, separated
by the subsystem they belong to. b. Placing the sun (middle) and planet gear spacers on the carrier. c. Placing the sun gears on the carriers. Stage 1 requires the sun gear shaft and Stage two the sun gear socket. Carrier spacer pictures off to the side of each carrier. d. Placement of the planet gears around the sun gear on the carrier. e. Placement of the carrier spacer on the bottom side of the carrier. f. Placement of the carrier assembly within the ring gear, completing Stage 1. g. Placement of the middle indicator on top of Stage 2’s sun gear. h. Comparison between Stage 1 and Stage 2 gear systems.

### The counter module

Relevant components:
- Sun gear shaft adapter (counter)
- Sun gear spacers (counter)
- Planet gears (counter)
- Planet gear spacers (counter)
- Ring gear (counter)
- Counter module planetary gear system
- Counter face
- Counter shell
- Counter knob

The counter planetary gear system
Follow steps 1 through 5 from the main planetary gear systems to construct the counter’s planetary gear system (see ‘Assembling the planetary gear systems’, Fig. S1.3a-d).

Assembly
1. Place the counter face piece face up on top of the carrier pegs. Make sure that the pegs slot into place on the bottom of the counter face (Fig. S1.3e).
2. Hold the gear assembly by the side pegs on the ring gear and insert the whole assembly face-up into the counter shell, by aligning the side pegs to the small notches on the shell.
3. Push the gear assembly all the way up inside the shell, then twist it to follow the notches until everything clicks into place (Fig. S1.3f). The gear assembly should not rotate within the shell if it has been inserted correctly.
4. Insert the knob into place on top of the counter module assembly and rotate the gear system until the ‘0’ marking aligns with the small arrow on top of the “number window”, then re-insert the knob so that the ‘0.00’ marking is on top (Fig. S1.3g, h).
5. Firmly push down on the knob so that it somewhat stays in place. The knob may fall out as there is no fastening which holds it in place.
6. Set the counter module aside (Fig. S1.3i).

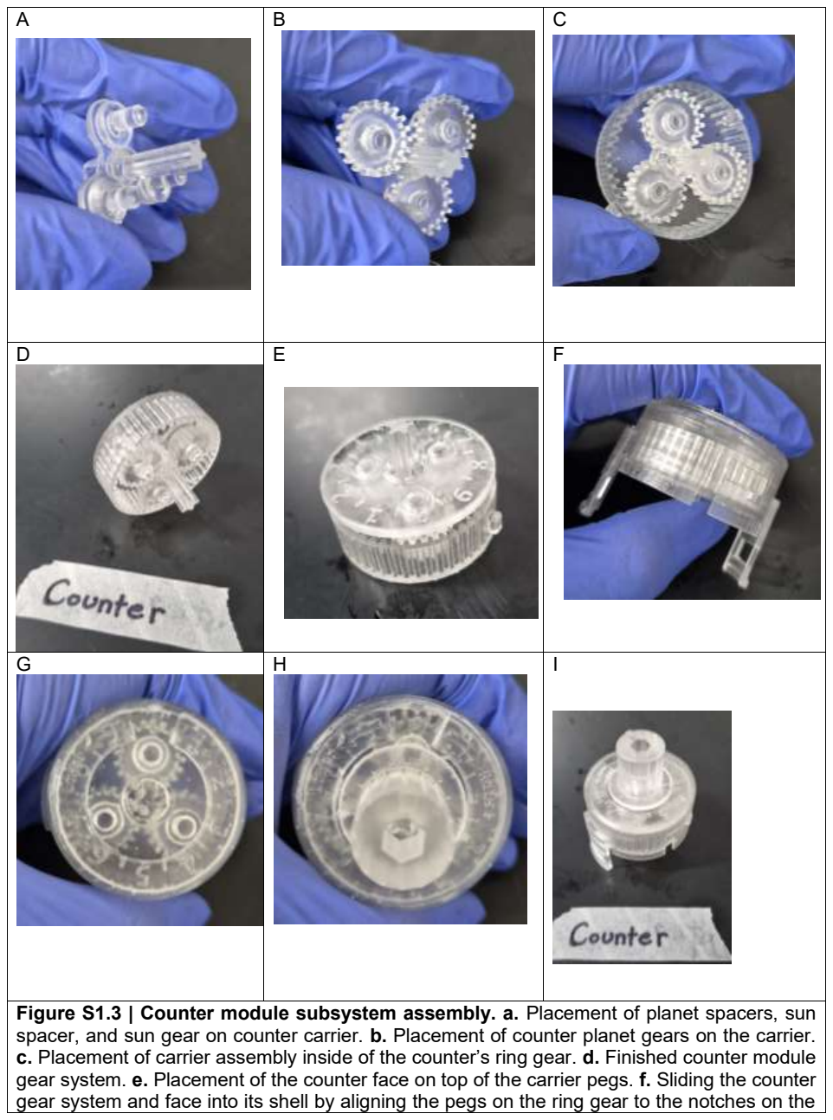
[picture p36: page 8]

A | B | C
D | E | F
G | H | I
Figure S1.3 | Counter module subsystem assembly. a. Placement of planet spacers, sun
spacer, and sun gear on counter carrier. b. Placement of counter planet gears on the carrier.
c. Placement of carrier assembly inside of the counter’s ring gear. d. Finished counter module gear system. e. Placement of the counter face on top of the carrier pegs. f. Sliding the counter gear system and face into its shell by aligning the pegs on the ring gear to the notches on the shell. g, h. Setting the counter system to zero (g) before placing the knob on top, also centred at 0 (h). i. Finished counter module.

### The screwdriver body

Relevant materials:
- Knob (small or large), x1 (if not using the counter module)
- Top casing shell, x1 (if not using the counter module)
- If using counter module, replace with the top casing shell for counter module
- Top casing, x1
- Bottom casing shell, x1
- Bottom casing, x1
- Bit adapter

Assembly instructions:
1. Insert the stage 1 planetary gear system (see ‘assembling the planetary gear systems’) into the top casing piece, and the stage 2 system into the bottom casing (Fig. 1.4a, b). Make sure you align the bottom of the ring gears to the patterns on both the casings so that the whole assembly slides fully into place.
2. Slide the bit adapter into the bottom casing shell from the inside (Fig. 1.4c). The bit adapter should not fall out when the shell is held right-side-up (the rat logo on the side should be right-side-up, Fig. 1.4d).
3. Slide the stage 1 gear system and bottom casing down the bottom casing shell so that the side pegs on the bottom casing go through the shell notches, twisting until everything slides into place (Fig. 1.4e). Set it aside.
4. Slide the stage 2 gear system and top casing in the same way (Fig. 1.4f).
5. Align the bottom shaft on the stage one gear system into the sun gear socket on the stage 2 system, then slide everything into place. Make sure that the side latches on sides of the two shells latch together (Fig. 1.4g).
a. If a counter module is used, repeat this with the top latches on the top casing shell (Fig. 1.4h).
b. If a counter module is not used, inset the regular knob on the top of the screwdriver.
6. Give the completed screwdriver a few turns to test if everything turns as it should.
7. Slide a 4 mm screwdriver bit into the bit adapter to use the Kepler driver (Fig. 1.4i).

A | B | C

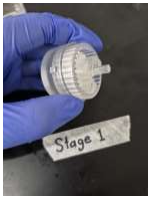
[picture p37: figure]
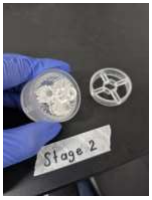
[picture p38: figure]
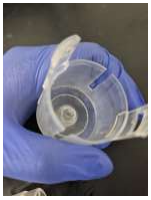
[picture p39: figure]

D | E | F

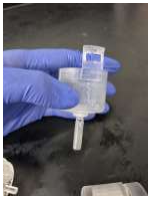
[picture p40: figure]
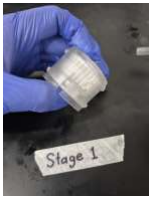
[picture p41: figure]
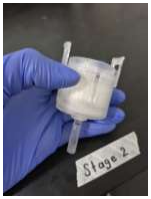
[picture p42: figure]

G | H | I

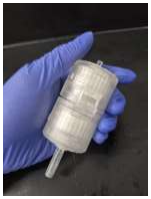
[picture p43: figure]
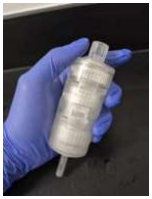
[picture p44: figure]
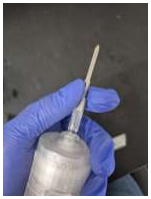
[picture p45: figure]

Figure S1.4 | Assembling the Kepler driver. a, b. Inserting the Stage 1 gear system into the
top casing (a) and the Stage 2 gear into the bottom casing (b). c, d. Inserting the bit adapter piece into the bottom casing shell (c). The bit adapter stays in place inside the bottom casing shell if placed correctly (d) e, f. Inserting the Stage 1 (e) and Stage 2 (f) gear assemblies into their respective shells. g. Mating of the Stage 1 and Stage 2 gear assemblies by snapping their shells together. The latches on the side hold the two modules together. h. Mating the counter module to the rest of the Kepler driver. i. Fitting a 4 mm hex screwdriver bit into the bit adapter.

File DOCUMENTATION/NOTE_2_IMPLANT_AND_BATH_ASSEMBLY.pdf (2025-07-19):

## Supplemental Note 2: Implant and saline bath assembly

Implant assembly can, in theory, be completed in as little as 4 hours. This is assuming that all parts have already been printed, washed, post-cured, and sanded, and that the probes have already been glued to the shuttle. The total assembly from printing to mounting can be completed over the course of 2 days otherwise. All implant pieces can be found in our GitHub repository (https://github.com/rjibanezalcala/EXPLORE).

Drilling

On the following implant components, drill a hole into the areas below (Fig. S2.1a) using the indicated drill bit size:
- Skull interface
- 1.0 mm: The holes in the middle of each of the 3 recessed hexagonal areas.
- Implant body
- 1.0 mm: The top bilateral sockets.
- 1.0 mm: The bottom bilateral sockets
- 1.0 mm: The bottom three screw holes
- 1.4 mm: The top drive screw hole.
- Probe shuttle
- 1.4 mm: The drive screw hole
- Headstage interface
- 1.0 mm: The bilateral screw holes on the bottom
- 1.0 mm: The single screw hole in the hex nut indent.
- (optional) 7/64 in: The bilateral holes above the screw holes
- Cap
- 1.0 mm: The single screw hole
- Surgery stereotactic holder
- 7/64 in: The two holes on either side of the holder.
- Shuttle stereotactic holder
- 1.4 mm: The drive screw hole

Threaded inserts and heat-setting

Heat-setting should happen as soon as possible between washing the 3D prints in IPA to remove excess uncured resin and the post-cure. This ensures malleability of the plastic and prevents cracking. A soldering iron set to about 200ºC seems to work well if the inserts are pushed in a slow, controlled manner.

- Probe shuttle
- Heat-set an M1.4 threaded insert into the only socket on the shuttle from the top. The insert should be flush with the body of the shuttle (Fig. S2.1b).
- Skull interface
- Heat-set or glue an M1 hex nut into each of the 3 recessed hexagonal areas (Fig. S2.1c). You may apply a thin layer of UV resin over the hex nuts to secure them in place if needed.
- Implant body
- Heat-set an M1 threaded insert onto each of the 2 sockets located on the top side of the implant body (Fig. S2.1d). Take extra care to do so slowly to minimise cracking of the plastic. If cracking does happen, fill the area in with UV resin.
- Heastage dock
- Heat-set one M1.4 thread into each of the 2 pre-drilled holes on the headstage interface, taking care to not push the insert all the way to the other side (Fig. S2.1e).

IMPORTANT: Make sure that threaded inserts are well bonded to the plastic and do not turn when a screw is screwed into them!

(Figure S2.1 on next page)

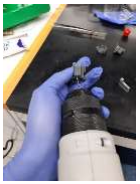
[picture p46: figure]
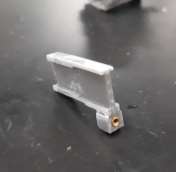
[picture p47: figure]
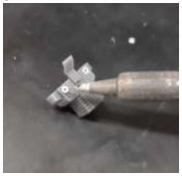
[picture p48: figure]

A | B | C

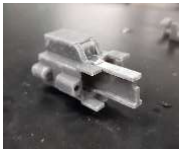
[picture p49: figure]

D | E | F

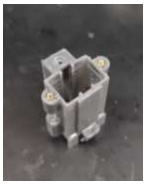
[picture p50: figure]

Figure S2.1 | Drilling and threaded inserts. a. Drilling of implant pieces to ensure
that screws, inserts, and wires fit in their respective receptacles. b. Shuttle with M1.4 threaded insert. c. Heat-setting three M1 nuts onto the skull interface, two pictured, one on the back. d. Two M1 inserts on the top of the implant body. e. Two M1.4 threaded inserts on the headstage interface. f. Fitting the shuttle into the implant body. The shuttle may need to be sanded with sandpaper in order for it to fit, however some amount of resistance to movement is desirable.

Sanding

The only piece which may need some amount of sanding with sandpaper is the shuttle. Sand the edges of this piece if it does not fit into the implant body (Fig. S2.1f). However, make sure that the shuttle still moves inside the implant with some resistance, as this will help stabilise the probes to prevent undesired movement and drift.

The grounding circuit

1. Use the 1.6 mm drill bit to drill two holes into the copper sheet. Cut two 4 mm x 4 mm sections around the holes and sand the edges down to create two small, round copper plates no more than 4 mm in diameter (Fig. S2.2a, b). You may use a hammer to flatten the segments if needed. Sand one side the copper plates to remove any coating the metal may have. Set these aside.
2. Remove the black insulating plastic around two pin connectors using wire cutters or pliers. The pin should have a long prong on the flat side, and a shorter prong on the rounded side. Set the two bare metallic pin connectors aside for now.
3. Cut four 6.5 cm segments of the PFA-coated wire. Use sandpaper to scrape off about 1 cm of the wire’s coating on each end. The wire cannot be soldered with the coating on. Set two segments aside.
4. Take two of the wire segments and carefully solder one end of each wire to the closed side of a socket connector (Fig. S2.2c, d). Be careful to not use too much solder as this may make fitting the socket connector into the implant difficult. If the socket connector or wire do not hold the solder well, use flux!
5. Use the soldering iron to tin both copper plates and solder one end of the remaining wire segments securely onto each of the plates (Fig. S2.2e, f). Take care to not solder over the hole you drilled. If the copper or wire do not hold the solder well, use flux! Finally, screw in a bone screw to test its fit, expand the holes using the drill if the screw does not go through. The screw should stay in place but be free to turn in place. Leave the screw in place for surgery.
6. Place a pin connector on each receptacle on the top of the skull interface rounded side first. Affix them using UV resin.
7. Solder the wire and copper plate assembly onto the pin connector from the bottom (Fig. S2.2g). Solder the wire parallel to the prong for a stronger bond. Use flux if you have difficulty soldering the two components together.
8. Thread each wire + socket connector assembly wire-first through the connector receptacles on either side of the bottom of the implant body and pull the wire through until the connector is inside the receptacle (Fig. S2.2h). If the pre-made channel is not wide enough, use the 1 mm drill bit to open it.
9. With the help of tweezers, thread the wire through the pre-drilled holes above the receptacles so that the wire comes out through the top of the casing from the inside (Fig. S2.2i). Use UV resin to cover the hole and the wire. This will affix the wire and socket connector in place and protect the inside of the implant. Tape down the excess wire on the top to the side of the implant body to move it out of the way when loading the probes (Fig. S2.2j).

A | B | C

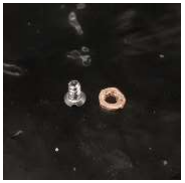
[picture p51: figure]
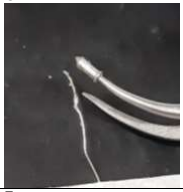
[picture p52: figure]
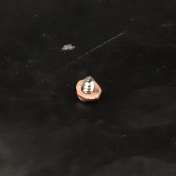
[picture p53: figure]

D | E | F

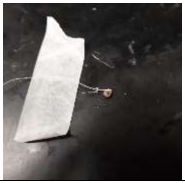
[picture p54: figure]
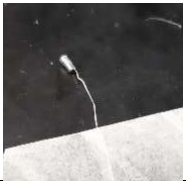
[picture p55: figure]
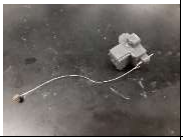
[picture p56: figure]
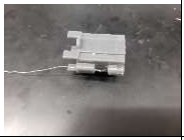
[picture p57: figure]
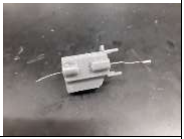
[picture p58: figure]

G | H | I

J

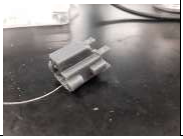
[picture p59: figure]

Figure S2.2 | Grounding circuit components. a. 4 mm diameter copper plate next to
a skull screw. b. Test fitting the skull screw with the copper plate. The skull screw should fit through the plate and be able to rotate freely. c, d. Soldering wire to socket connector. The wire is soldered parallel to the side of the connector to increase strength of the joint. e, f. Soldering the wire to the copper plate, using tape to hold the wire down. g. Soldering the copper plate and wire to a pin connector inserted into the skull screw. h. Threading the socket connector and wire though the bottom pin receptacle on the implant body. i. Threading wire through the side pinhole on the implant body. j. Moving the wire to the side of the implant body, so it doesn’t interfere with assembly of the implant.

Post-curing

Post-curing parameters will vary depending on your resin specifications. For Formlabs Tough 2000 resin, we used a Form Cure at 60ºC for 60 minutes, as per manufacturer’s recommendations. Please check your resin post-curing specifications.

Probe preparation

We use silicone glue to affix the probes onto the probe shuttle because it is strong and is water resistant, in addition to being flexible enough to be removed if the probes need to be removed from the shuttle for any reason. Silicone glue starts curing fairly quickly! Make sure to work quickly during this step as partially-cured glue will not hold as well.

IMPORTANT: The probes will be exposed to damage at this stage. Make sure to take all possible precautions to avoid breaking the probe shanks. Wear gloves and use anti-electrostatic discharge equipment to prevent electrical damage to the probes.

1. Apply silicone glue to the probe shuttle on one side. Carefully take one probe and press it against the glue while gently sliding it forward so that the probe catches onto the front stops on the shuttle. Carefully flip the shuttle over and repeat this with a second probe (Fig. S2.3a).
2. Place the shuttle and probes back into the box that the probes came in, held in between two of the foam pads. Set aside and allow the glue to cure for 24 hours.

Mounting the probes onto the implant

1. Mount the stereotactic shuttle holder onto one of the stereotactic arms then raise the DV as far up as possible. Place a M1.4 x 4 screw into the screw hole.
2. Mount the skull interface onto the holding bay. Place the holding bay down beneath the stereotactic device arm. Secure the holding bay in place with tape or a M6 x 15 screw if appropriate (Fig. S2.3b).
3. Carefully take the shuttle with the probes attached out of the box and slide them into the holder.
4. Using a screwdriver, turn the M1.4 x 4 screw clockwise until it catches and pulls the shuttle fully into the holder.

WARNING: The probes will be extremely vulnerable to damage at this point. Take care to not manoeuvre anything underneath the probes or you may risk breaking the probes.

5. Carefully manoeuvre the shuttle around and into the skull interface; when lowering it, monitor the probe shank using the surgical microscope.
6. Lower the implant body onto the assembly carefully; first turn the casing slightly so that the probe’s ribbon FPC connectors fit all the way through, then turn it again so that the drive screw receptacle lines up with the drive screw cover on the skull interface. Press the down until the screw holes line up with the M1 nut threads.
7. Screw in all three mating points between the skull interface and shuttle casing with M1x4 screws, starting by the vertical one (Fig. S2.3c).
8. Short the Ground and Reference pads on the probes with wire, then solder one of the ground wires to the pads to complete the ground circuit; repeat on the other probe. Do not solder the two probes together, each probe should have its own ground.
9. Insert the drive screw into the drive screw receptacle on the shuttle casing and turn it clockwise to retract the probe. Fold the FPC ribbon and ground wire into the implant, letting the connector stick out from the top.
10.Lower the headstage interface onto the FPC connectors so that they thread through the slots. Have the connectors stick out about 5 mm from the top of the interface and drop the two ribbon pinchers into the headstage interface. Screw in a M1.4x4 screw on either side to pinch the connectors and hold them onto the middle spacer on the interface. Take care not to screw them in too much as the plastic may break.
11.When every piece of the implant is securely fastened in place, take the implant off the holding block and slightly lower the probe by turning the drive screw counterclockwise. Inspect the shanks under light to verify their integrity (Fig. S2.3d, e).
12.Place the headstage interface cap on if desired, however the cap must be removed prior to implantation in order to mount the implant onto the surgery stereotactic holder and to access the drive screw.
13.Keep the built implant on the holding bay until implantation.
14.In preparation for the surgery, mount the implant onto the surgery stereotactic holder (Fig. S2.3f) with the probes fully retracted for protection.
A | B | C

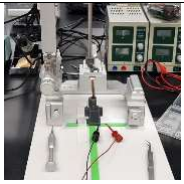
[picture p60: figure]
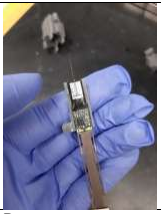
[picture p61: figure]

D | E | F

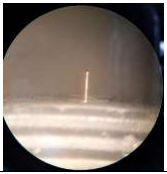
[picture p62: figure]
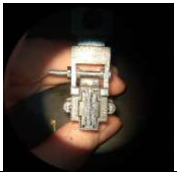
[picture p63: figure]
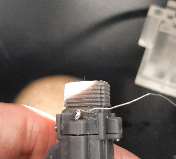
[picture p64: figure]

Figure S2.3 | Probe mounting. a. Glueing the probe to the shuttle piece with
silicon glue, typically takes at least 12 hours to dry enough to continue. b. Preparing for the mounting procedure using a stereotaxic device. The shuttle and probe are placed in the shuttle holder and the skull interface is placed on the holding block below it. The shuttle and probe are then maneuvered into place while monitoring the probe’s shank with a surgical microscope. c. After the probe has been mounted, the rest of the implant is assembled on the holding block to protect the probe shank. d, e. The probe is lowered slightly to verify the integrity of the shank under the surgical microscope. f. The implant is firmly mounted onto the implant holder in preparation for surgery.

Calibrating the implant

Calibrating the implant is a crucial step to ensure that downward probe displacements are done accurately. If calibration is omitted, the probe shank may not reach the targeted areas, and displacements might be different from implant to implant. This is due to errors in the 3D printing process, particularly when printing pieces with overhangs. This error has typically been measured to be about +0.5 mm with our printer, but it may be different if using other printers. Additionally, a padding distance has been added to the implant’s design to ensure that probe can be retracted fully into the implant despite the error, for protection. The total added distance introduced by these two factors is referred to hereon as the “error”.

The goal of calibration is to eliminate the error and provide a known starting point for further probe displacements. This process must be done after assembly, but prior to surgery. We provide a custom calibration block (Fig. S2.4a) to facilitate the calibration process. To calibrate an implant, follow the instructions below:

1. Mark your screwdriver bit on one of the faces of the hexagonal shaft with a marker. This will help you keep track of the number of turns you’ve made.
2. Retract the probes fully inside the implant by turning the drive screw clockwise (cw). The screw will become difficult to turn when the probe and shuttle are at their highest position, though take care to not over-tighten it. Make note of the bit and screw’s positions; this will be your reference.
3. Place the implant on the calibration block (Fig. S2.4b, c). The bottom opening of the implant (where the probe shanks come out) should be pointing in the direction of the arrows on the block.
4. Turn the drive screw 10 times and compare the position of the tip of the shank against the block’s reference line labeled “3 mm”. Use a microscope or magnifying goggles to do so. It is unlikely that they will align (Fig. S2.4d).

NOTE: The calibration block was designed with a drive screw pitch of 0.3 mm in mind, this is why the reference line is placed at 3 mm from the edge of the skull connector opening. If your drive screw pitch is different, you will need to edit the calibration block with the appropriate Blender file. (https://github.com/rjibanezalcala/EXPLORE/tree/a34436c046cc62e7382828ab8184ebb5ed3a1f90/BLENDER)

5. Under magnification, keep turning the screw until the tip aligns with the center of the mark. Keep track of how many times you have turned the screw; this number will be the corrective turns (corr) to eliminate the error.
6. Retract the probes and back to the position from step 2. Turn the screw corr times. The tip should barely be visible from above, as it will align with the edge of the skull connector opening (Fig. S2.4e).
7. To verify calibration, turn the screw 10 more times. If the error has been correctly eliminated, the tip should align with the 3 mm mark (Fig. S2.4f). If this is the case, the implant has been calibrated.
a. If the tip does not align with the mark, verify that the drive screw pitch is 0.3 mm and repeat steps 2-7.

NOTE: It is recommended that you retract the probes fully before surgery. The Excel surgery log (https://github.com/rjibanezalcala/EXPLORE/blob/main/SURGERY_KIT/EXPLORE_surgical_calculator_blank.xlsx) contains a field where you may input the corr turns and calculate the error in micrometers. This will be added to further recorded displacements, but it is always a good idea to record the error elsewhere.

A | B | C

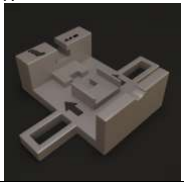
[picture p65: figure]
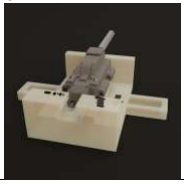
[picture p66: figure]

D | E | F


Figure S2.4 | Implant calibration. a. The calibration block. b-c. Correct
placement of the implant on the calibration block. d. Uncalibrated implant. The drive screw is turned 10 times, and the tip of the probe shank is compared against the 3 mm reference line. The tip does not align with the implant pictured.
e. Tip position after calculating and eliminating the vertical displacement variance. The implant and calibration block have been tilted backward to visualize the probe tip aligned with the skull connector’s opening threshold. f. Calibrated implant after turning the drive screw 10 times starting from the position pictured in (e). The tip now aligns with the center of the 3 mm reference line.

Assembling the saline bath

Assembling the saline bath is as simple as cutting two copper plates (10 mm x 19.5 mm), running a wire through each tube from the front, then soldering the wires to the plates. The length of the wire can be 20 - 30 cm or more, if desired. We crimped one banana connector to each wire end to ensure compatibility with the A.M.P.I. Iso-flex Electrical stimulus isolator. (https://www.ampi.co.il/iso-flex) We recommend affixing the copper plates with silicone sealant and letting it dry for at least 24 hours to ensure a watertight seal.
